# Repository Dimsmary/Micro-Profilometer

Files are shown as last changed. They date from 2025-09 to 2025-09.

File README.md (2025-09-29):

# Micro-Profilometer 微米级轮廓仪

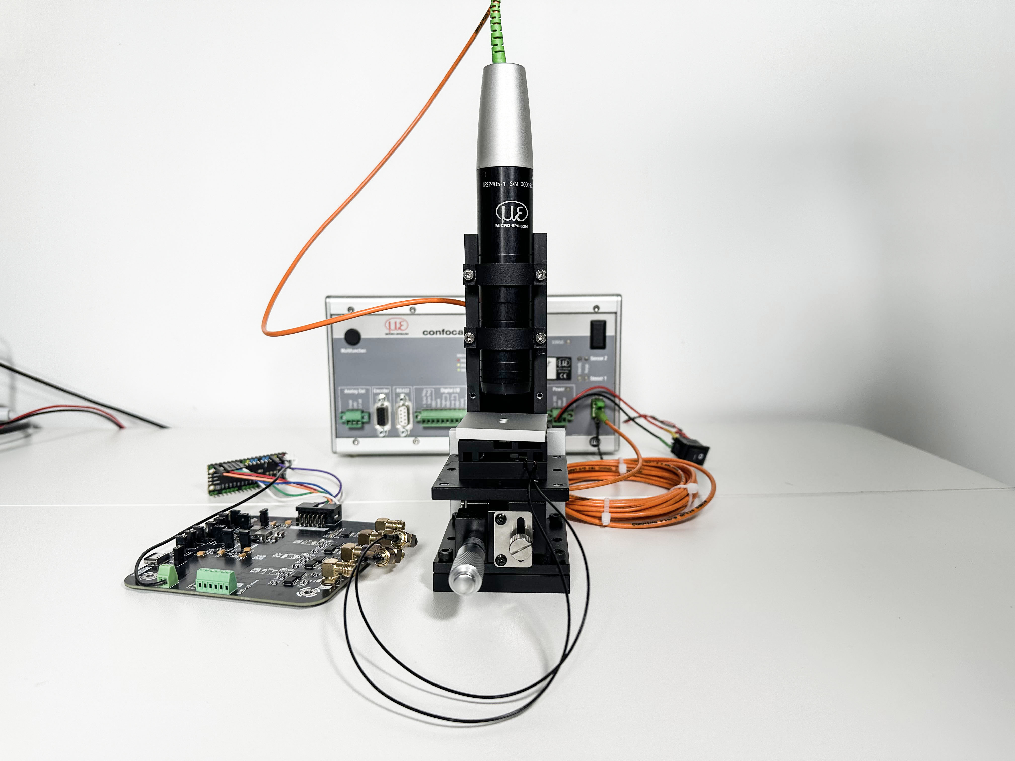
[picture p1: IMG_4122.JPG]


**[中文](README.md) | [English](README_ENG.md)**

## 项目简介

本项目主要设计了一个**亚微米级定位台**，通过与Micro-Epsilon共聚焦位移传感器进行结合后，设计成为微米级表面轮廓仪。

1、该轮廓仪能够完成对微小样品的表面轮廓测量（如晶圆裸片、金属表面等），分析其表面平整度或起伏结构。动态深度分辨率能够达到38nm，横纵分辨率能够达到8μm。

2、对于亚纳米级定位台，其分辨率能够达到100nm。基于该定位台，能够实现包括但不限于：扫描成像（如本项目所示的轮廓仪）、微流控操纵、光学对准等功能。

## 性能表现

### 亚微米级定位台

该定位台为基于粘-滑效应工作原理，具体分析可参考文章：

Open STM: A low-cost scanning tunneling microscope with a fast approach method

https://www.sciencedirect.com/science/article/pii/S2468067223001116

Low-cost, open-source XYZ nanopositioner for high-precision analytical applications

https://www.sciencedirect.com/science/article/pii/S2468067222000621

位移测试通过IFC2421共聚焦位移传感器与IFS2405-1探头完成，采样率为1ksps。

#### 最小步长（5V锯齿波）

在对压电陶瓷施加5Vp-p的锯齿波时，定位台所产生的位移为100nm左右。

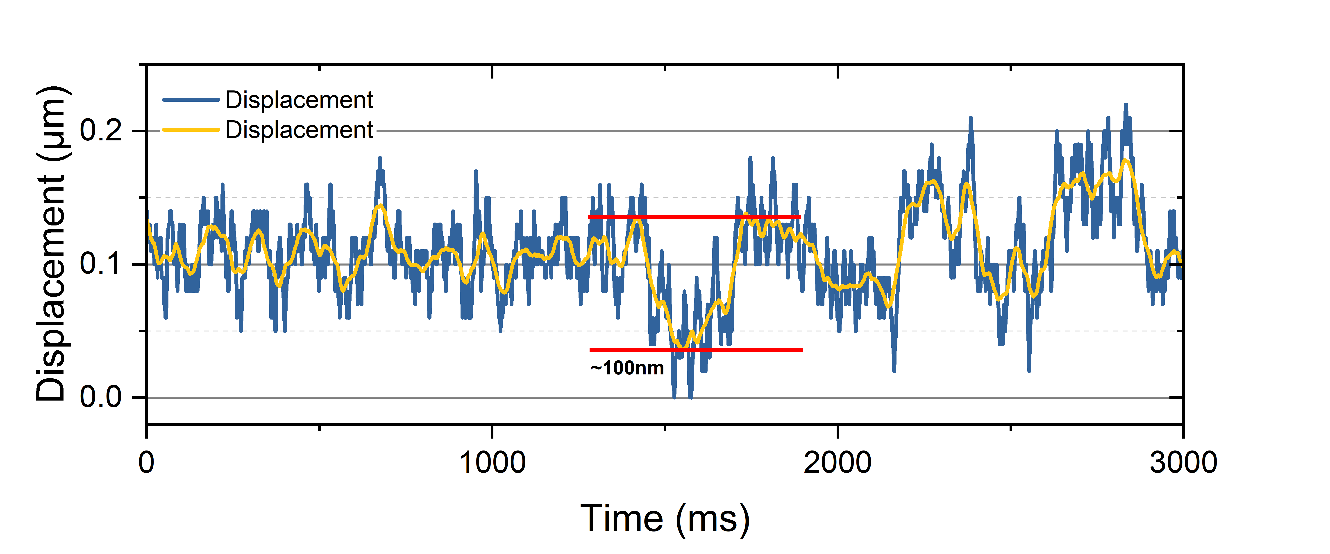
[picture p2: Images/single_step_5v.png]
Single Step 5V


#### 稳定步长（10V锯齿波）

在实际测试过程中，过低的锯齿波电压可能导致位移的不稳定。随着驱动电压的增加，定位台的位移将趋于稳定，以下是10V锯齿波驱动下的单步位移情况。（对于无需反向移动的情况，基于AL1.65型压电陶瓷的单步电压可增加至20Vp-p）

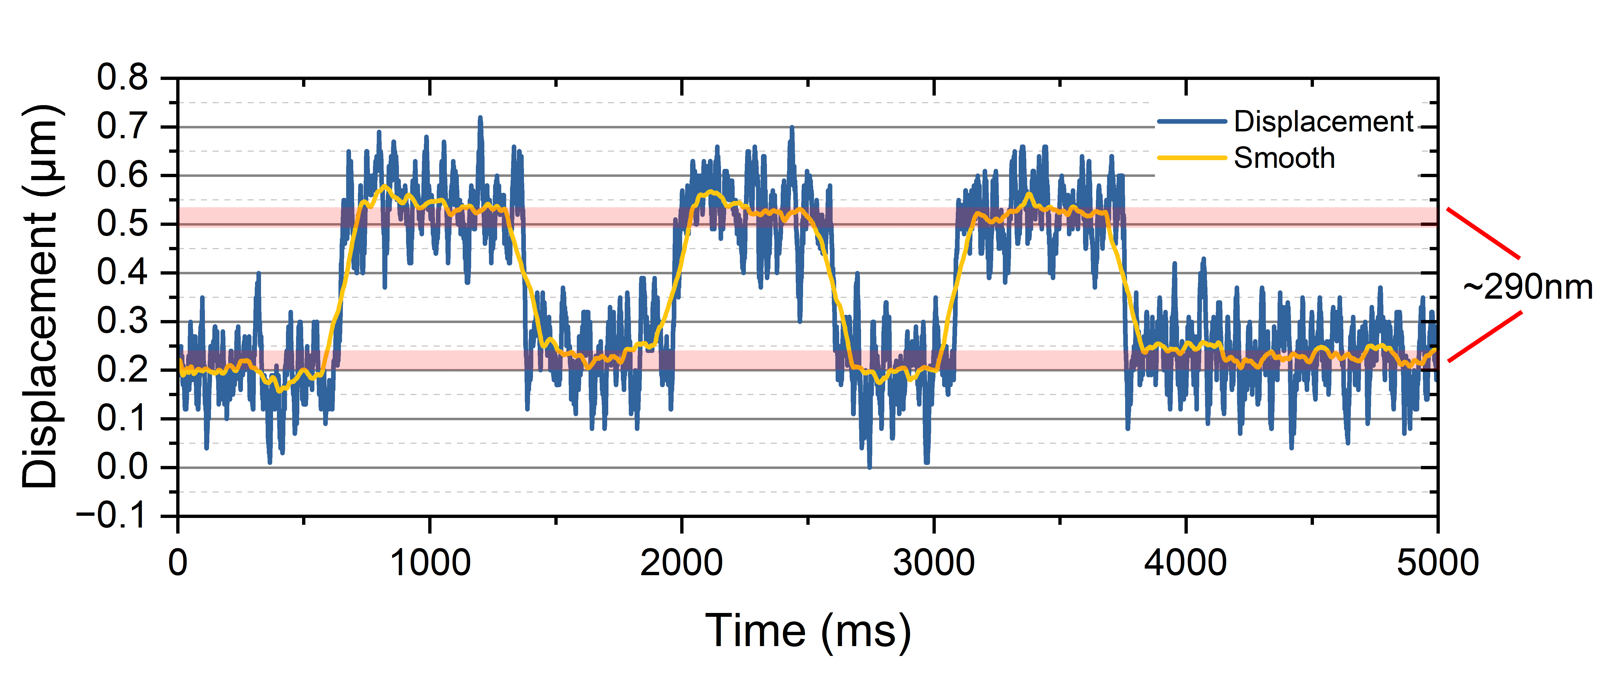
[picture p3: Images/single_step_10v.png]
Single Step 10V


#### 稳定步长（10V锯齿波x10）

通过施加10个连续的10V锯齿波，可以实现2μm左右的单向稳定位移。

在下图所示的过程中，反向位移略小于正向位移，这可能是磁铁与滑轨产生了倾斜导致的。在部分的测试结果中，正向与方向位移能够接近。

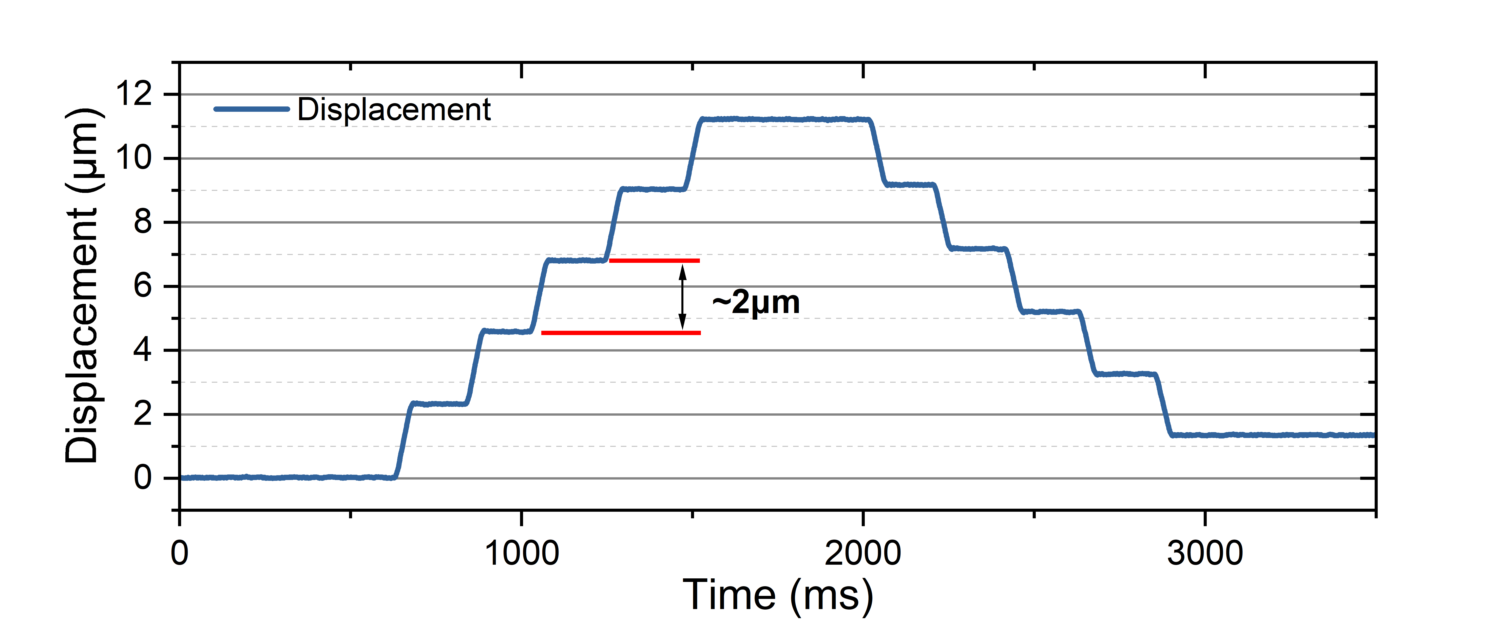
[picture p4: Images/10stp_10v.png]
10Steps 10V


#### 最高速度测试

通过改变锯齿波斜率，测试定位台能够达到的最高速度。如下图所示，定位台的最高速度能够大大0.85mm/s。

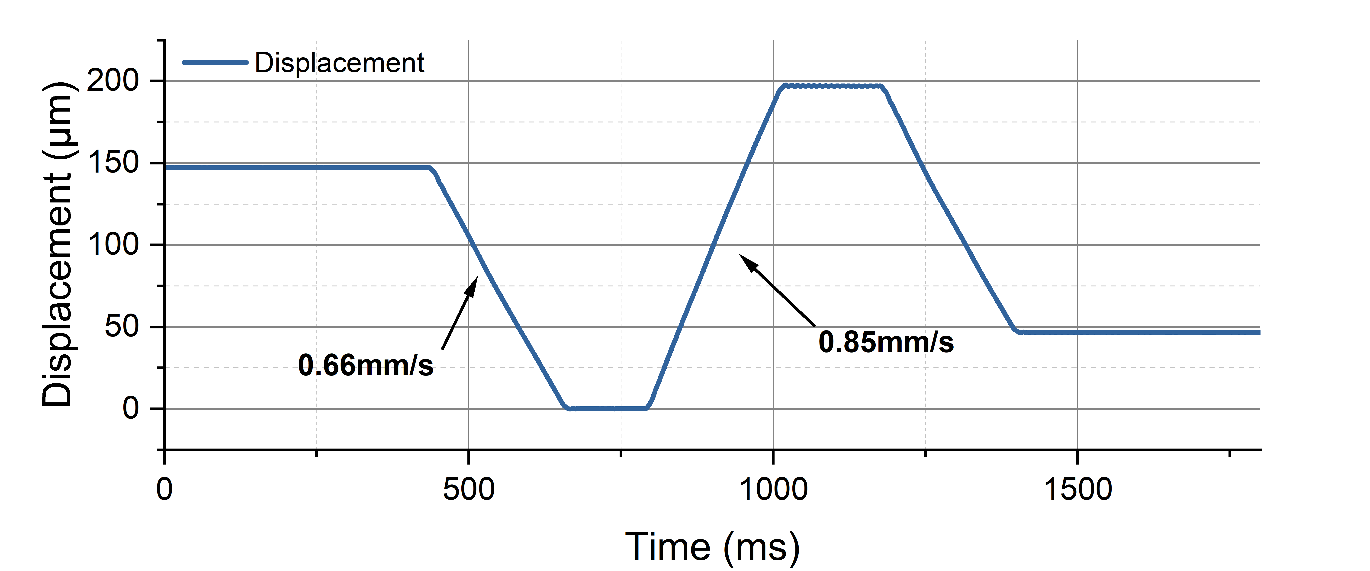
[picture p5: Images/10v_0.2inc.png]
Speed Test


### 微米级轮廓仪

通过将定位台与共聚焦位移传感器结合，设计成为微米级轮廓仪。在工作过程中，定位台进行蛇形扫描，共聚焦传感器采集位移数据，经上位机整合后采集成图像。注意，以下图片的单位**均为微米**。

原始数据可以在ScanImages>RawImage中被找到。其中，xxxs.tiff为灰度映射至[0~255]的版本，以方便直接查看。原始图像需要使用Gwyddion或其他相关软件进行查看。

#### 晶圆裸片

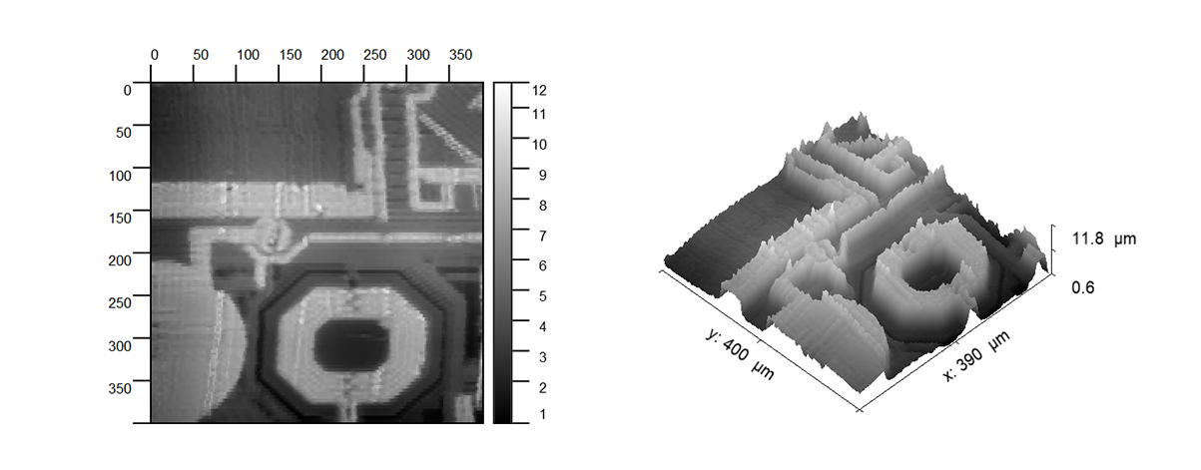
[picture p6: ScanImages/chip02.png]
chip02


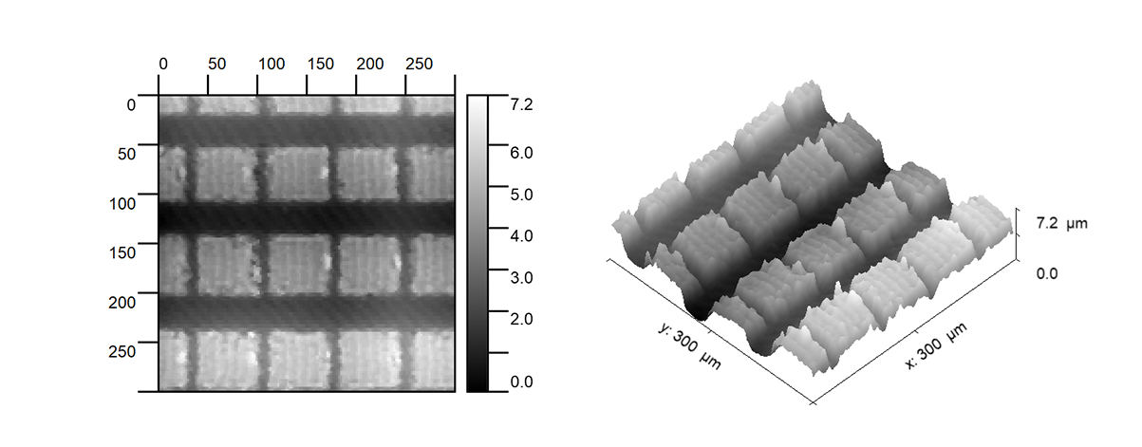
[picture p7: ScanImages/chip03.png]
chip03


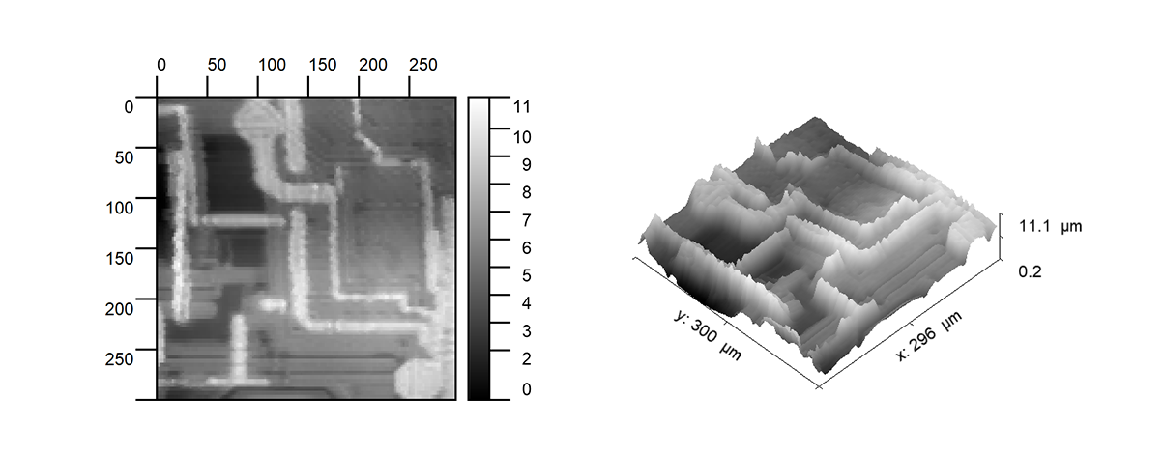
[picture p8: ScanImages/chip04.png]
chip04


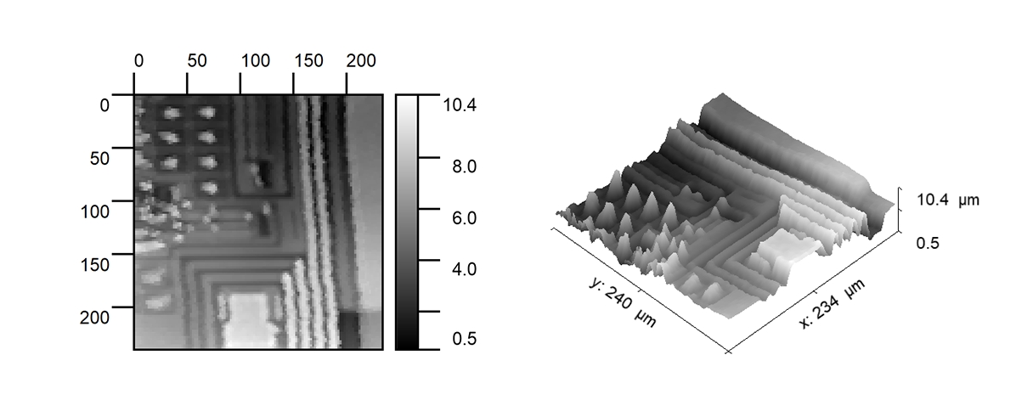
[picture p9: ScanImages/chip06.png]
chip06


#### 阳极氧化铝表面

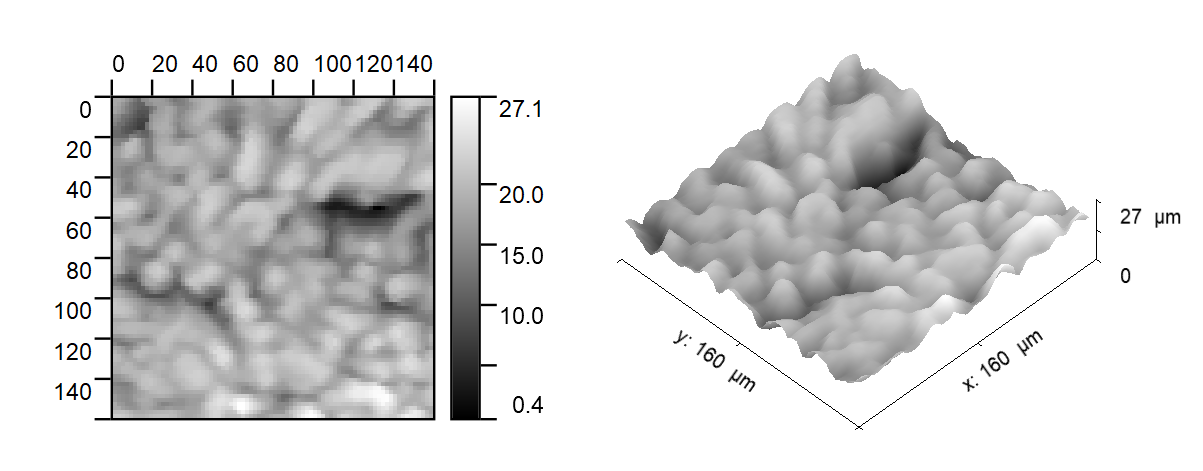
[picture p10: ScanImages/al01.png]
al01


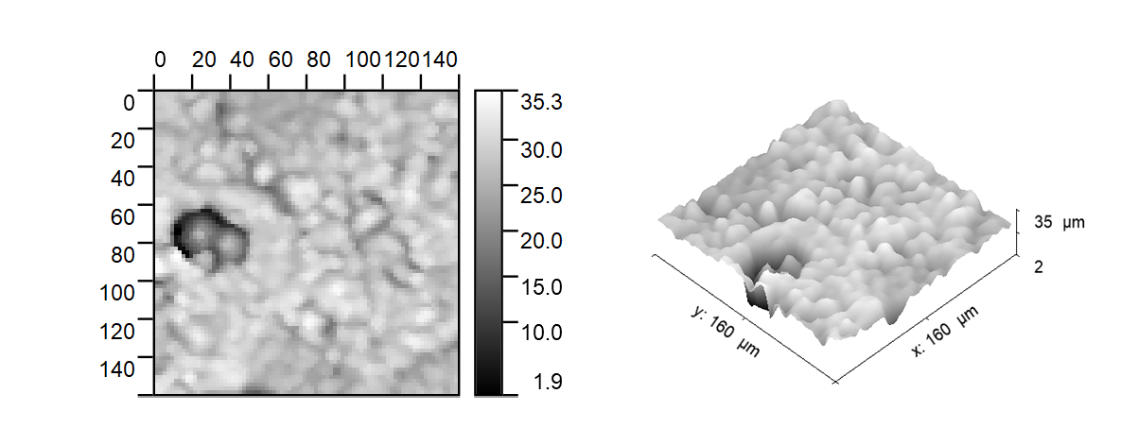
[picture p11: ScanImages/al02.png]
al02


#### 苹果表面

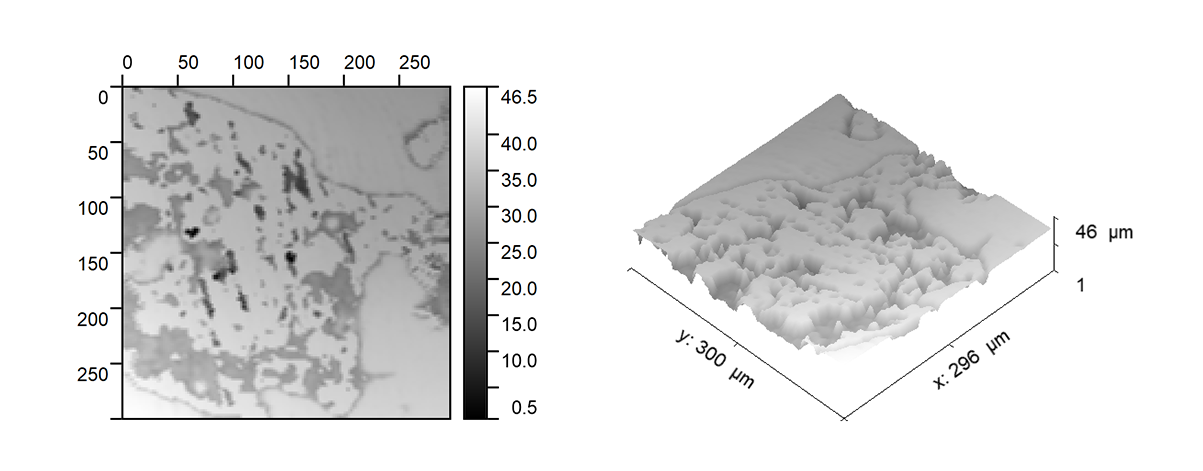
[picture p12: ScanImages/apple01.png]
apple01


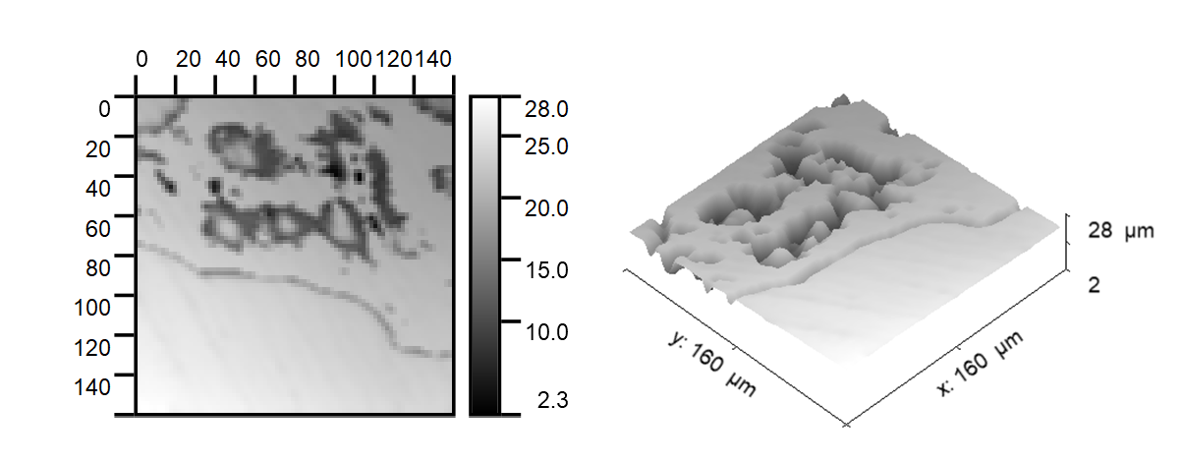
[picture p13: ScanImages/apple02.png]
apple02


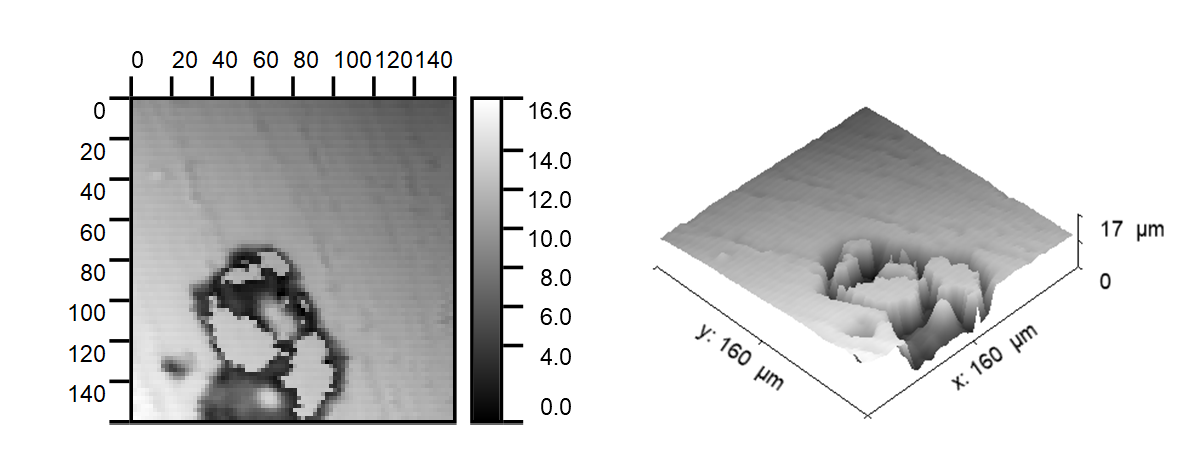
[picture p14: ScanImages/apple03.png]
apple03


#### 纸张表面

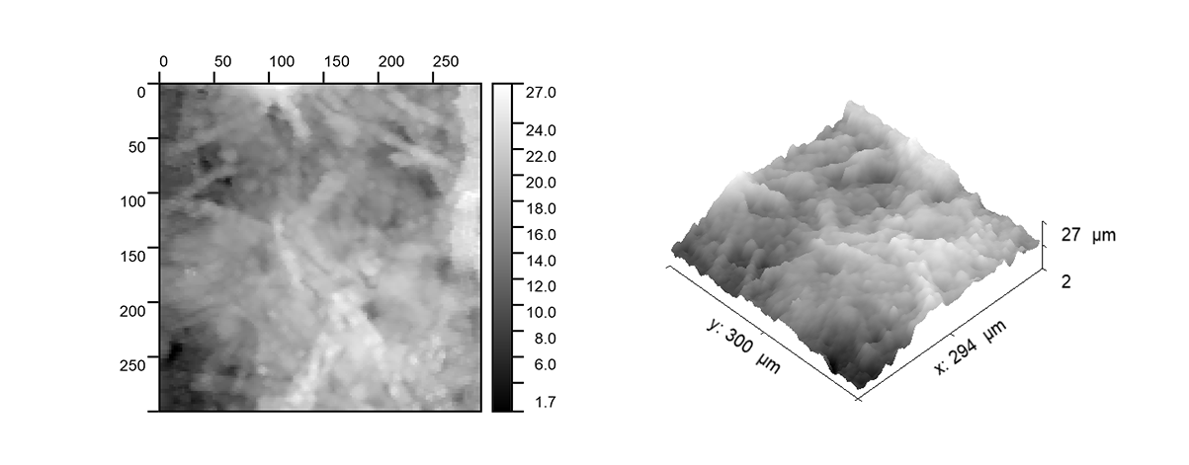
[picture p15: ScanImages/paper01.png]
paper01


#### 纸巾表面

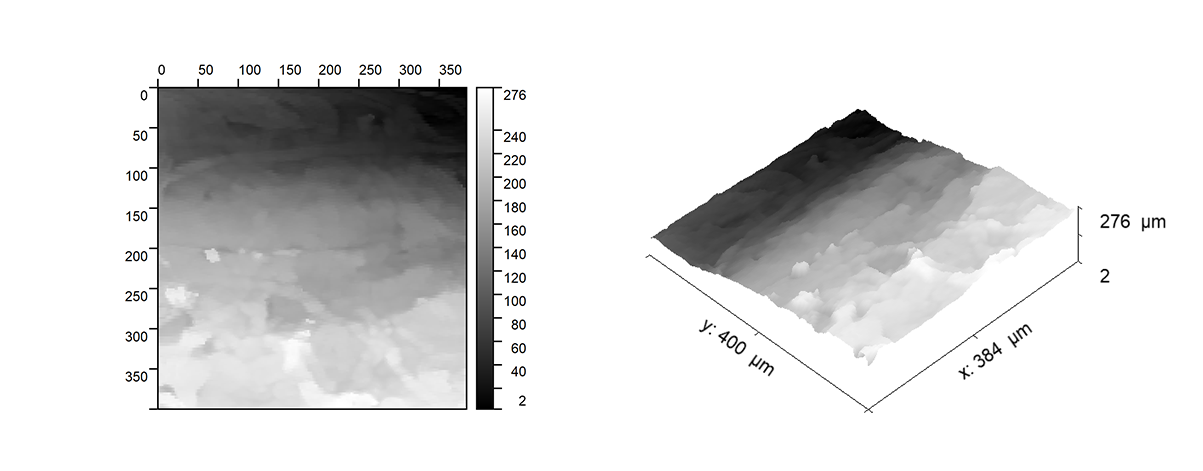
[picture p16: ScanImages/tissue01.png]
tissue01


## 文件目录介绍

3DModel > 包含了项目所有的3D文件

3DModel > CNC > 包含了项目需要加工的CNC文件

3DModel > SolidWorks > 包含了项目的3D原始工程文件

ControlSoftware > 包含了项目使用到的脚本，请安装requirements.txt对应的pip包后运行gui.py以启动上位机

ControlSoftware > reverse.py 用于高度反转

Images > 包含压电滑台的性能数据

Pico2Firmware > 树莓派Pico2固件

ScanImages > 轮廓仪的扫描原始结果

PCB > 工程的PCB文件，请使用EasyEDA/立创EDA打开。或在线打开：https://oshwhub.com/dimsmary/micron-profilometer-micro-profil

## 复刻步骤

### PCB复刻

按照PCB文件夹下提供的文件进行复刻即可。有以下注意事项：

- 对于+5V LDO、DAC3、ADC区域电路为非必要部分，如无需求，可不进行焊接。
- 对于DAC部分的电路，如果DAC采用AD5761R，则ADR421可不进行焊接。如果采用AD5761，则需要进行焊接。对于本项目，默认采用AD5761R。AD5761R与AD5761在寄存器操作时略有不同，后续将进行介绍。

### 固件烧录

请使用VS Code打开Pico2Firmware>Table_Movement进行烧录，或使用Pico2Firmware目录下的.uf2文件完成烧录。

如果需要修改AD5761/AD5761R的初始化设置，请修改Table_Movement>lib>ad57x1>ad57x1.cpp中的\#define CONTROL_REG_BASE，该宏定义对AD5761/AD5761R的初始化进行了设置，包括内部参考电压源的开启/关闭，详情请参考对于数据手册的CONTROL REGISTER小节。

### 零件组装

所有需要加工的文件被放置在了3DModel > CNC下，请参考视频[链接待更新]或3DModel > SolidWorks下的XYTable.SLDASM以及full_assemble.SLDASM进行组装。

- 对于需要额外购买的Z轴定位台，其关键词为[Z轴升降台]，台面尺寸为60x60cm，行程为1cm。

- 对于fix.STEP，可以采用3D打印。
- 定位台的组装可参考[OpenSTM项目](https://github.com/Dimsmary/OpenSTM)，或对应的HardwareX文章：https://doi.org/10.1016/j.ohx.2023.e00504。需要注意的是，在组装定位台时，需要将磁铁侧壁打磨光滑，否则定位台的行程可能受到影响。
- PCB中的Connector通过M2螺丝安装在XYTable_X中，G连接压电陶瓷的负极，X/Y连接压电陶瓷的正极。对于Y轴压电陶瓷的走线已预留槽位，可使用漆包线连接至此PCB。

## 使用方法

### 控制板设置与连接

#### 电源跳线设置

对于PCB电源跳线帽部分的连接，其顺序为（对于三脚，不连则为选择中间，连接中间与另外一端则为选择另外一端）：

SYNC/FREQ: 2.4M

SEQ: SEQ.

SLEW: NORM.

EN1:ON

EN2:OFF

SS: 连接

V_EN: 连接

COMP1: GND

COMP2: GND

#### 数据线连接

SYN1、SYN2连接至GPIO17、20，SDI2、SCK2连接至SPI0的数据输出、时钟引脚。

#### 电源连接

使用5V Type-C口电源连接至Power_IN端。

#### 与定位台的连接

使用SMA-IPEX连接线，将DAC0、DAC1与定位台中的Connector PCB连接。

### PC-USB连接

将PICO2连接至PC，此时PICO2将在PC处初始化两个虚拟串口。

使用RS422转USB连接Micro-Epsilon共聚焦位移传感器与PC，在Micro-Epsilon的设置中，需要设置仅输出Distance1。

### 上位机使用

运行gui.py启动上位机。

上位机包含四个选项卡：Serial Ports, DAC Manual Control, Sawtooth Control, Scan。

#### Serial Ports

在Serial Ports中，moving table port连接PICO2的虚拟串口，连接数字较大的一个。（如，PICO2提供了COM12和COM13，连接COM13）。confocal port连接RS422转USB。

#### DAC Manual Control

在DAC Manual Control中，可以对DAC0/1的输出电压控制。如果需要控制DAC3，可以将SYN3连接至GPIO21。

#### Sawtooth Control

在Sawtooth Control中，可以控制DAC0/1发送锯齿波。以下是参数解释：

Sawtooth Steps：锯齿波数量。

Increment：电压每步增量，单位：V。

Maximum Voltage：锯齿波电压峰值。

Bias Voltage：锯齿波初始电压。

Channel Select：输出端口选择，X channel则为DAC0，Y Channel则为DAC1。

在参数修改后，需要点击Sync Settings进行参数同步。

点击Send Positive Sawtooth则会发送正锯齿波，Send Negative Sawtooth则会发送负锯齿波。

#### Scan

在Scan中，可以对样品轮廓进行扫描。

X Forward Steps：扫描过程中，X定位台的单步前进的锯齿波数。

X Backward Steps：扫描过程中，X定位台的单步后退锯齿波数。

Y Forward Steps：扫描过程中，Y定位台的单步前进锯齿波数。

Y Backward Steps：暂时不使用

Image Size X：图像X尺寸

Image Size Y：图像Y尺寸

Increment：暂时不使用

点击Start Monitor后，共聚焦传感器的位移值将实时显示在图像框的上方。将各参数值设置好后，点击Scan开始扫描。

需要注意的是，考虑到定位台的正向位移和反向位移可能不一致，可以设置不同的X Forward/Backward Steps值。当你观察到图像不对劲时，可以尝试保持Forward值，然后增加或减少Backward值直到图像正常。

在完成扫描后，图像将被显示在图像框中，点击Save Image即可对图像进行保存。图像将被保存为两张，其中带_scaled后缀的图像的灰度值将被映射至0~255以便浏览。

## 最后

如果你有任何问题，欢迎提交Issue。

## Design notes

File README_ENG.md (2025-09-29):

# Micro-Profilometer



**[中文](README.md) | [English](README_ENG.md)**

## Project Overview

This project primarily designs a **sub-micron positioning stage**. By integrating it with a Micro-Epsilon confocal displacement sensor, it is developed into a micron-level surface profilometer.

1. This profilometer can measure the surface profile of small samples (such as wafer dies, metal surfaces, etc.), analyzing their surface flatness or topographic features. It achieves a dynamic depth resolution of 38nm and lateral resolutions of 8μm.
2. For the sub-micron positioning stage, its resolution reaches 100nm. Based on this stage, various functions can be implemented, including but not limited to: scanning imaging (as demonstrated by this profilometer project), microfluidic manipulation, optical alignment, etc.

## Performance

### Sub-Micron Positioning Stage

This positioning stage operates based on the stick-slip principle. For detailed analysis, please refer to the articles:

Open STM: A low-cost scanning tunneling microscope with a fast approach method

https://www.sciencedirect.com/science/article/pii/S2468067223001116

Low-cost, open-source XYZ nanopositioner for high-precision analytical applications

https://www.sciencedirect.com/science/article/pii/S2468067222000621

Displacement testing was completed using an IFC2421 confocal displacement sensor with an IFS2405-1 probe, at a sampling rate of 1 ksps.

#### Minimum Step (5V Sawtooth Wave)

When a 5Vp-p sawtooth wave is applied to the piezoelectric ceramic, the displacement generated by the positioning stage is about 100nm.

Single Step 5V

#### Stable Step (10V Sawtooth Wave)

During practical testing, excessively low sawtooth wave voltage may lead to unstable displacement. As the driving voltage increases, the stage's displacement becomes more stable. The following shows the single-step displacement under a 10V sawtooth wave drive. (For scenarios not requiring reverse movement, the single-step voltage for the AL1.65 type piezoelectric ceramic can be increased up to 20Vp-p).

Single Step 10V

#### Stable Steps (10V Sawtooth Wave x10)

By applying 10 consecutive 10V sawtooth waves, a unidirectional stable displacement of about 2μm can be achieved.

In the process shown below, the reverse displacement is slightly less than the forward displacement, which might be caused by tilting between the magnet and the slide rail. In some test results, the forward and reverse displacements can be close.

10Steps 10V

#### Maximum Speed Test

By changing the slope of the sawtooth wave, the maximum speed achievable by the positioning stage was tested. As shown below, the maximum speed of the stage can reach 0.85 mm/s.

Speed Test

### Micron-Level Profilometer

By integrating the positioning stage with the confocal displacement sensor, a micron-level profilometer is constructed. During operation, the positioning stage performs a raster scan, the confocal sensor collects displacement data, and the host computer integrates this data to form an image. Note that the units in the following images are **all in micrometers**.

Raw data can be found in `ScanImages > RawImage`. Among them, files with the `xxxs.tiff` suffix are versions with grayscale mapped to [0~255] for direct viewing. The original images need to be viewed using Gwyddion or other relevant software.

#### Wafer Die

chip02

chip03

chip04

chip06

#### Anodized Aluminum Surface

al01

al02

#### Apple Surface

apple01

apple02

apple03

#### Paper Surface

paper01

#### Tissue Paper Surface

tissue01

## Directory Structure

`3DModel` > Contains all 3D files for the project

`3DModel > CNC` > Contains CNC files required for project fabrication

`3DModel > SolidWorks` > Contains the original 3D engineering files for the project

`ControlSoftware` > Contains scripts used in the project. Please install the pip packages listed in `requirements.txt` and run `gui.py` to start the host computer software.

`ControlSoftware > reverse.py` > Used for height inversion.

`Images` > Contains performance data for the piezoelectric stage.

`Pico2Firmware` > Raspberry Pi Pico 2 firmware.

`ScanImages` > Raw scanning results from the profilometer.

`PCB` > PCB files for the project. Please open using EasyEDA/JiLiang EDA. Or open online:https://oshwhub.com/dimsmary/micron-profilometer-micro-profil

## Replication Steps

### PCB Replication

- Replicate according to the files provided in the PCB folder. Note the following:
  - The circuits for the +5V LDO, DAC3, and ADC areas are non-essential and can be left unsoldered if not required.
  - For the DAC section circuit: If using the AD5761R DAC, the ADR421 does not need to be soldered. If using the AD5761, it must be soldered. This project defaults to using the AD5761R. Note that register operations for the AD5761R and AD5761 differ slightly; this will be explained later.

### Firmware Flashing

Please use VS Code to open `Pico2Firmware > Table_Movement` for flashing, or use the `.uf2` file in the `Pico2Firmware` directory to flash.

If you need to modify the AD5761/AD5761R initialization settings, please modify the `#define CONTROL_REG_BASE` in `Table_Movement > lib > ad57x1 > ad57x1.cpp`. This macro definition sets the initialization for the AD5761/AD5761R, including enabling/disabling the internal reference voltage source. Please refer to the CONTROL REGISTER section of the respective datasheet for details.

### Parts Assembly

- All files requiring machining are located in `3DModel > CNC`. Please refer to the video [Link to be updated] or the `XYTable.SLDASM` and `full_assemble.SLDASM` files under `3DModel > SolidWorks` for assembly.
  - For the additionally purchasable Z-axis stage, search using the keyword `[Z-axis lifting stage]`, with a platform size of 60x60mm and a travel of 1cm.
  - For `fix.STEP`, 3D printing can be used.
  - The assembly of the positioning stage can refer to the [OpenSTM project](https://github.com/Dimsmary/OpenSTM), or the corresponding HardwareX article: https://doi.org/10.1016/j.ohx.2023.e00504. Note that when assembling the positioning stage, the sidewalls of the magnets need to be polished smooth, otherwise the travel range of the stage might be affected.
  - The Connector on the PCB is mounted on the `XYTable_X` using M2 screws. `G` connects to the negative terminal of the piezoelectric ceramic, `X`/`Y` connect to the positive terminals of the piezoelectric ceramics. A slot is reserved for the wiring of the Y-axis piezoelectric ceramic; use enameled wire to connect it to this PCB.

## Usage Instructions

### Control Board Setup and Connection

#### Power Jumper Settings

For the PCB power jumper cap connections, the order is as follows (for three-pin headers, not connecting means selecting the middle pin; connecting the middle and another pin selects that other pin):

- SYNC/FREQ: 2.4M
- SEQ: SEQ.
- SLEW: NORM.
- EN1: ON
- EN2: OFF
- SS: Connect
- V_EN: Connect
- COMP1: GND
- COMP2: GND

#### Data Cable Connection

Connect SYN1, SYN2 to GPIO17, GPIO20. Connect SDI2, SCK2 to the data output and clock pins of SPI0.

#### Power Connection

Use a 5V Type-C power supply connected to the `Power_IN` terminal.

#### Connection to the Positioning Stage

Use SMA-to-IPEX cables to connect DAC0, DAC1 to the Connector PCB on the positioning stage.

#### PC-USB Connection

Connect the PICO2 to the PC. The PICO2 will initialize two virtual COM ports on the PC.

Connect the Micro-Epsilon confocal displacement sensor to the PC using an RS422-to-USB converter. In the Micro-Epsilon settings, configure it to output only `Distance1`.

### Host Computer Software Usage

Run `gui.py` to start the host computer software.

The software interface contains four tabs: `Serial Ports`, `DAC Manual Control`, `Sawtooth Control`, `Scan`.

#### Serial Ports

In the `Serial Ports` tab, connect `moving table port` to the virtual COM port of the PICO2 (connect to the higher numbered port, e.g., if PICO2 provides COM12 and COM13, connect to COM13). Connect `confocal port` to the RS422-to-USB converter.

#### DAC Manual Control

In the `DAC Manual Control` tab, you can manually control the output voltage of DAC0/1. If you need to control DAC3, connect SYN3 to GPIO21.

#### Sawtooth Control

In the `Sawtooth Control` tab, you can control DAC0/1 to send sawtooth waves. Parameter explanations:

- `Sawtooth Steps`: Number of sawtooth waves.
- `Increment`: Voltage increment per step, unit: V.
- `Maximum Voltage`: Peak voltage of the sawtooth wave.
- `Bias Voltage`: Initial voltage of the sawtooth wave.
- `Channel Select`: Output port selection, `X channel` is DAC0, `Y Channel` is DAC1.

After modifying parameters, click `Sync Settings` to synchronize the parameters.

Click `Send Positive Sawtooth` to send a positive sawtooth wave, and `Send Negative Sawtooth` to send a negative sawtooth wave.

#### Scan

In the `Scan` tab, you can perform a raster scan of the sample surface.

- `X Forward Steps`: Number of sawtooth waves for the single-step forward movement of the X stage during scanning.
- `X Backward Steps`: Number of sawtooth waves for the single-step backward movement of the X stage during scanning.
- `Y Forward Steps`: Number of sawtooth waves for the single-step forward movement of the Y stage during scanning.
- `Y Backward Steps`: Not currently used.
- `Image Size X`: Image size in the X dimension.
- `Image Size Y`: Image size in the Y dimension.
- `Increment`: Not currently used.

Click `Start Monitor` to display the real-time displacement value from the confocal sensor above the image box. After setting all parameter values, click `Scan` to start the scan.

Note: Considering that the forward and reverse displacements of the positioning stage might not be equal, you can set different values for `X Forward Steps` and `X Backward Steps`. If you observe that the image looks distorted, try keeping the `Forward` value and then increasing or decreasing the `Backward` value until the image appears normal.

After the scan is complete, the image will be displayed in the image box. Click `Save Image` to save the image. Two images will be saved; the one with the `_scaled` suffix has its grayscale values mapped to 0~255 for easier viewing.

## Finally

If you have any questions, please feel free to submit an Issue.

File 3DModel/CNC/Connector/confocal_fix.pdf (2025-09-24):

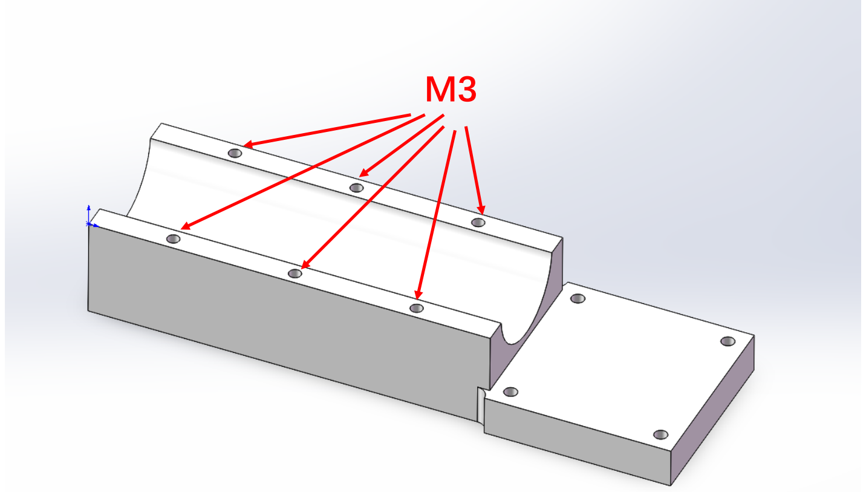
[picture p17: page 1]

M3

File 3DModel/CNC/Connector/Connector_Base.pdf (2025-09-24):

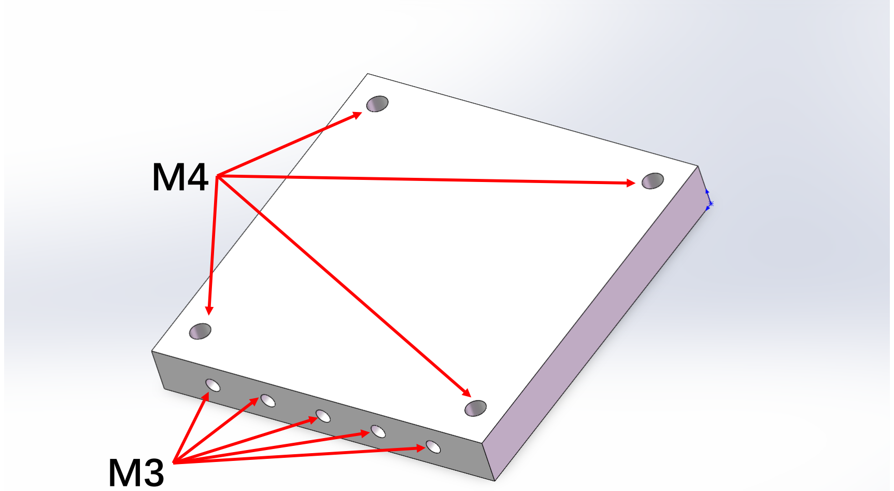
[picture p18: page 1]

M4

M3

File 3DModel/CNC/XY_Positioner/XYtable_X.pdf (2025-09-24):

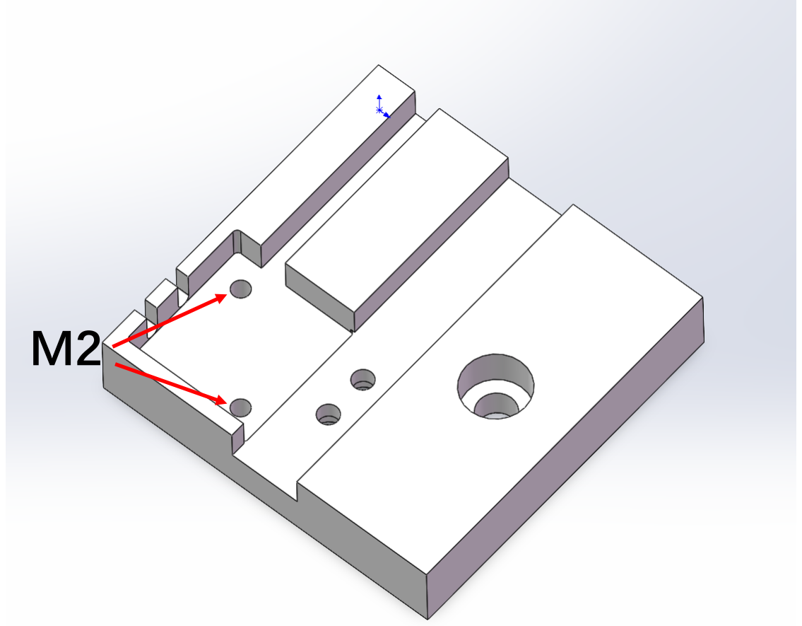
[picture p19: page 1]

M2

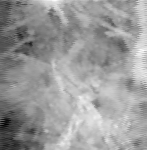
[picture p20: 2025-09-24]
ScanImages/RawImage/paper01.tiff

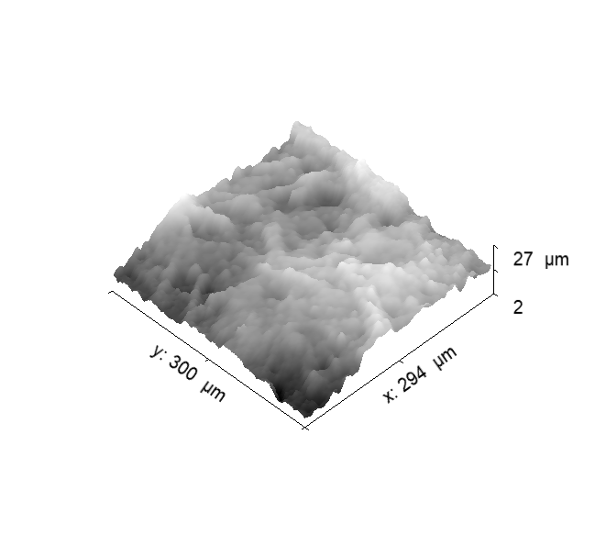
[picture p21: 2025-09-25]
ScanImages/Processed/paper01.png

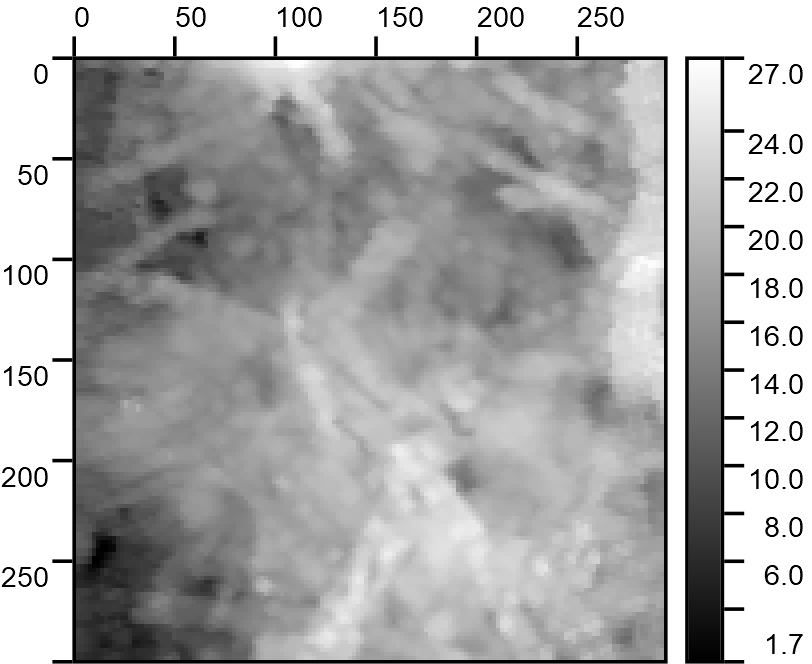
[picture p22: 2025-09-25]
ScanImages/Processed/paper01.tiff

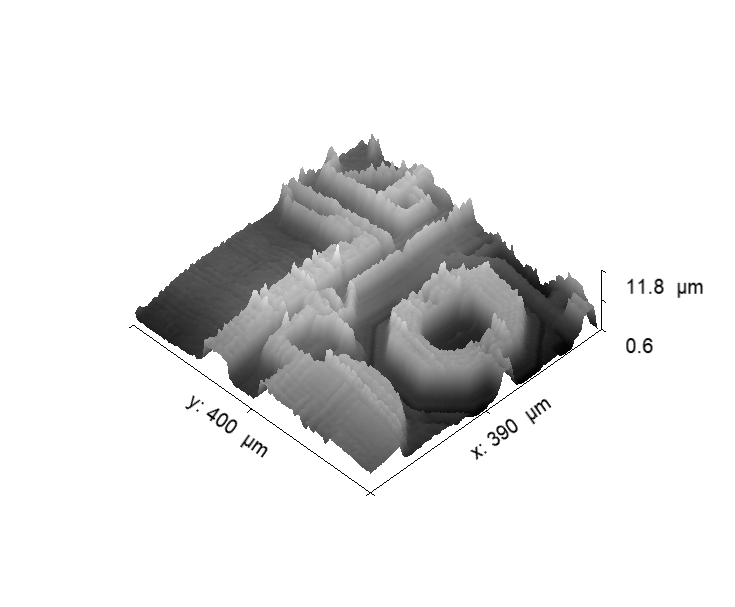
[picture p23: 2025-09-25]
ScanImages/Processed/chip02.png

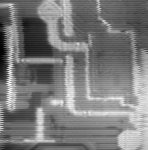
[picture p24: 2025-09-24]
ScanImages/RawImage/chip04s.tiff

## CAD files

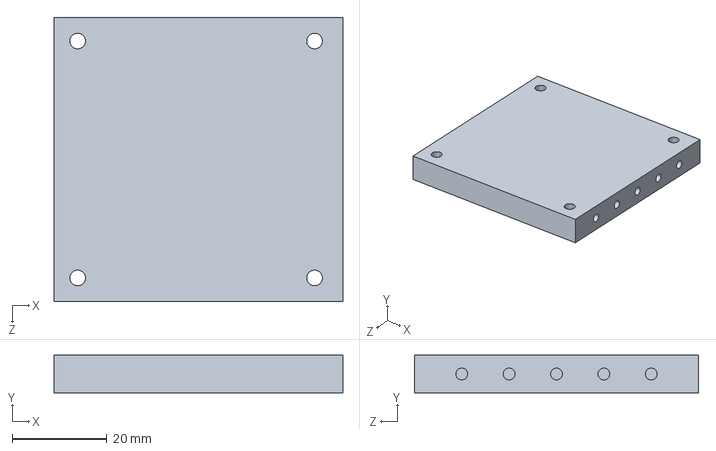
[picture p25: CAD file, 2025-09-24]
3DModel/CNC/Connector/Connector_Base.STEP
61.0 x 8.00 x 60.0 mm

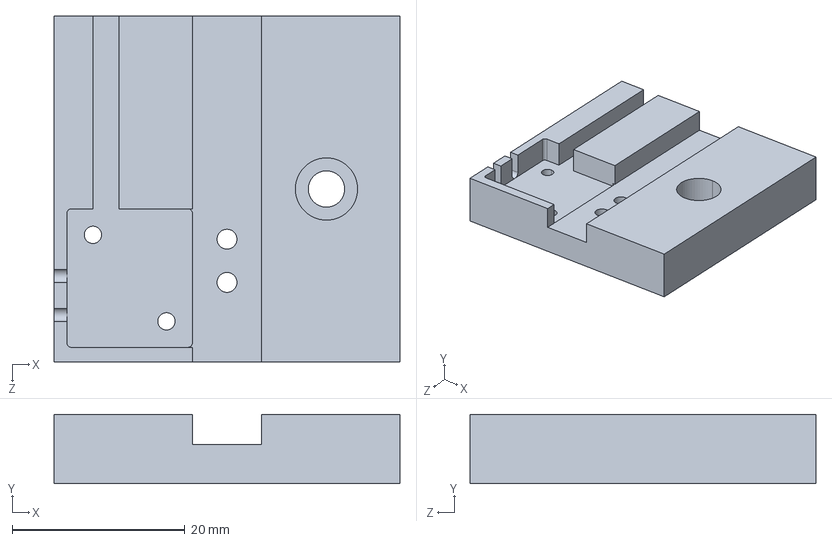
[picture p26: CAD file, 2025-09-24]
3DModel/CNC/XY_Positioner/XYTable_X.STEP
40.0 x 8.00 x 40.0 mm

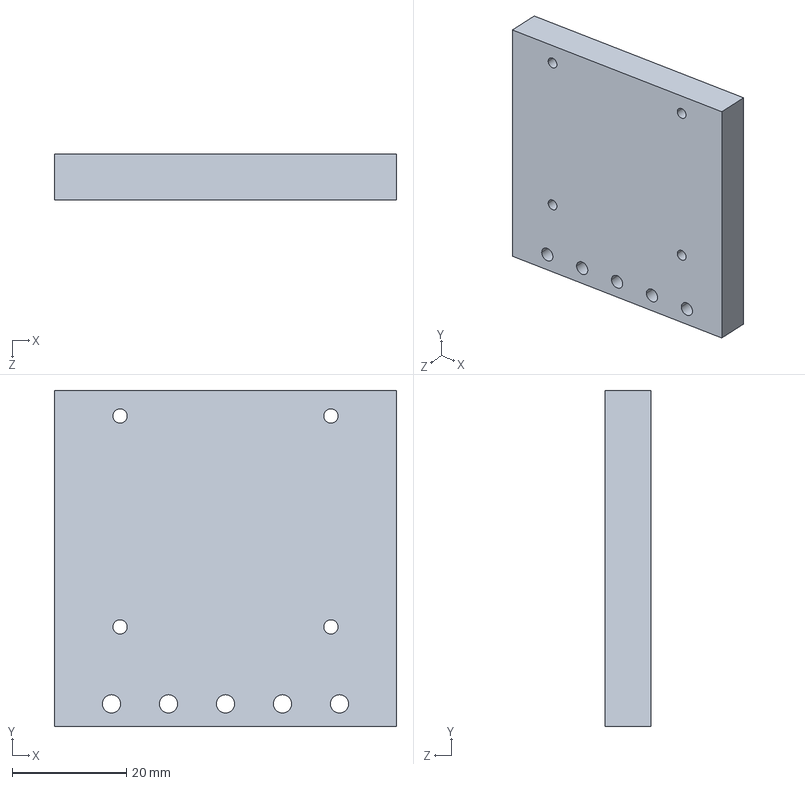
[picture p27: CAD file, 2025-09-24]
3DModel/CNC/Connector/Connector_Side.STEP
60.0 x 59.0 x 8.00 mm

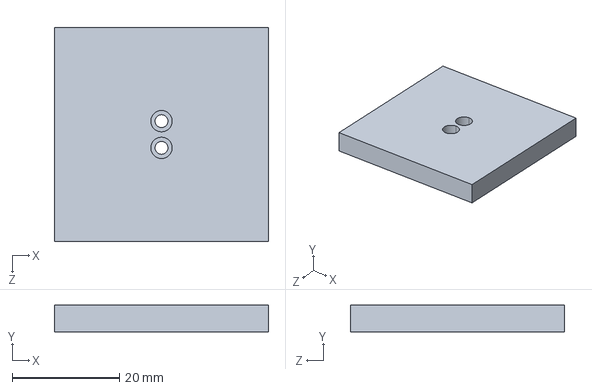
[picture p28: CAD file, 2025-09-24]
3DModel/CNC/XY_Positioner/XYTable_Table.STEP
40.0 x 5.00 x 40.0 mm

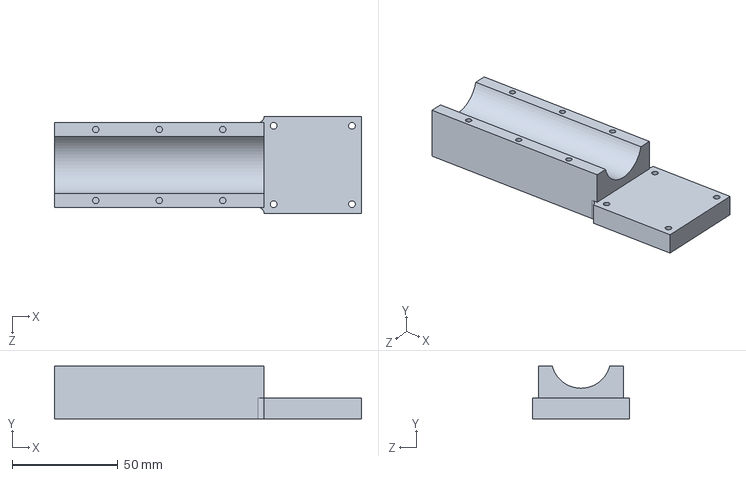
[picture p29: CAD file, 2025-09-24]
3DModel/CNC/Connector/confocal_fix.STEP
145.0 x 25.0 x 46.0 mm

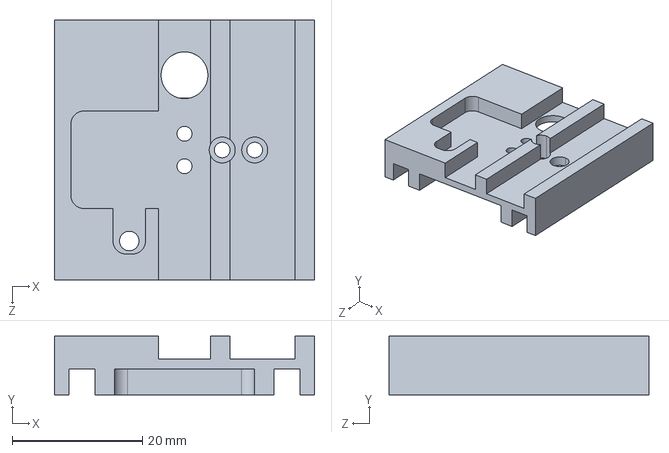
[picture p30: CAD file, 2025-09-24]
3DModel/CNC/XY_Positioner/XYTable_Y.STEP
40.0 x 9.00 x 40.0 mm

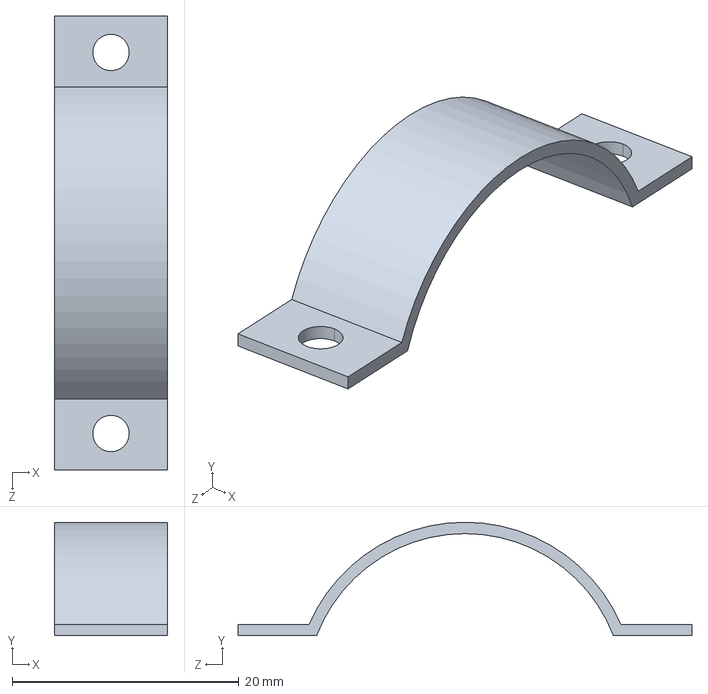
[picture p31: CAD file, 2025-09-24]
3DModel/CNC/Connector/fix.STEP
10.0 x 10.0 x 40.0 mm

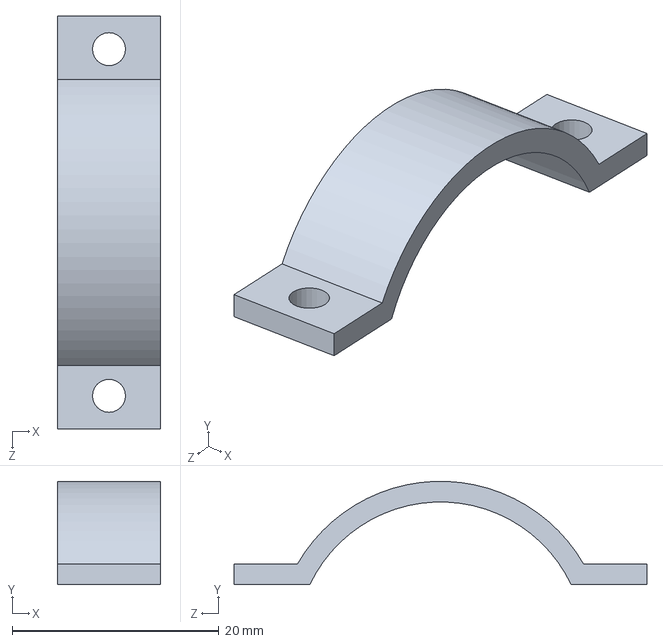
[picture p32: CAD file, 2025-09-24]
3DModel/Solidworks/fix.SLDPRT
10.0 x 9.99 x 40.0 mm

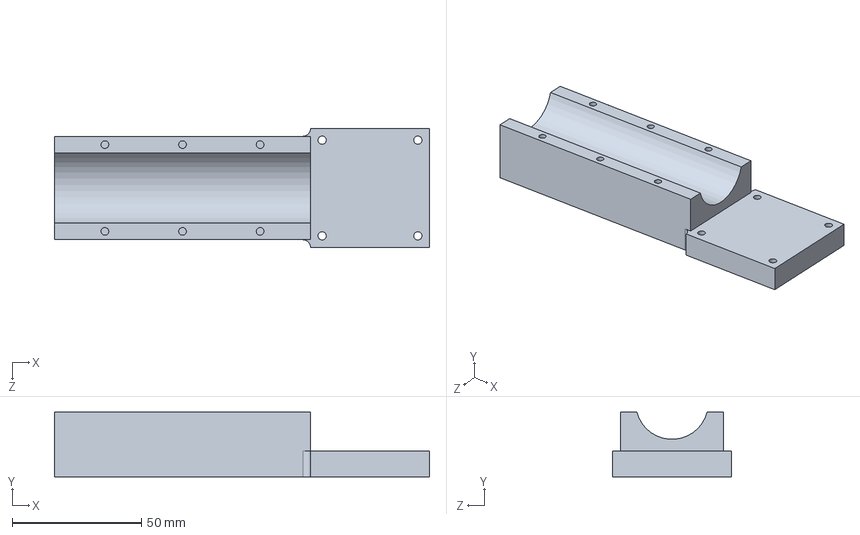
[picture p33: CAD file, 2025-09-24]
3DModel/Solidworks/confocal_fix.SLDPRT
145.0 x 25.0 x 46.0 mm

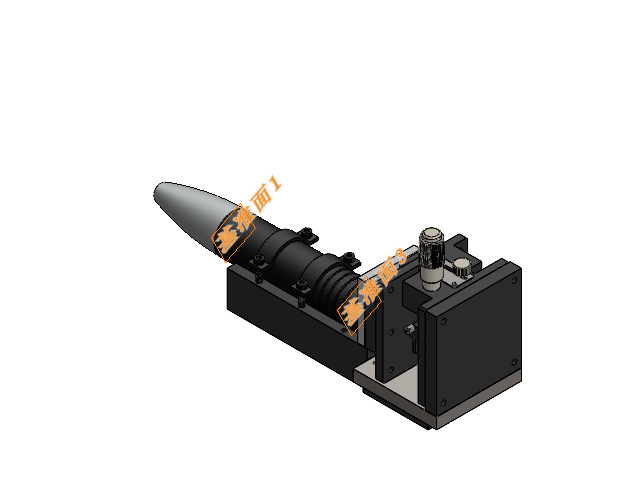
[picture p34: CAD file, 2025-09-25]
3DModel/SolidWorks/full_assemble.SLDASM
confocal_fix
Connector_Side
screw_M3-10 x 4
confocal
fix x 2
screw_M3-15 x 4
Connector_Base
ztable
XYTable_X
XYTable_Y
Slider_Bottom x 2
Slider_up x 2
XYTable_Table
screw_M2-4 x 4
pzt x 2
round_megnent x 2

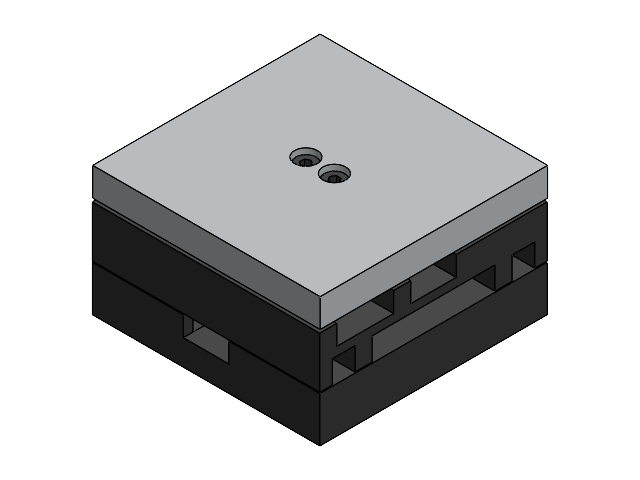
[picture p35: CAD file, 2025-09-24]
3DModel/Solidworks/XYTable.SLDASM
XYTable_X
XYTable_Y
Slider_Bottom x 2
Slider_up x 2
XYTable_Table
screw_M2-4 x 4
pzt x 2
round_megnent x 2

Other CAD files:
3DModel/Solidworks/XYTable_X.SLDPRT
3DModel/Solidworks/XYTable_Y.SLDPRT
3DModel/Solidworks/Connector_Side.SLDPRT
3DModel/Solidworks/XYTable_Table.SLDPRT
3DModel/Solidworks/Connector_Base.SLDPRT

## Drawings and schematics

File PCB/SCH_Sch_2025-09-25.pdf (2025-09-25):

# +12V LDO

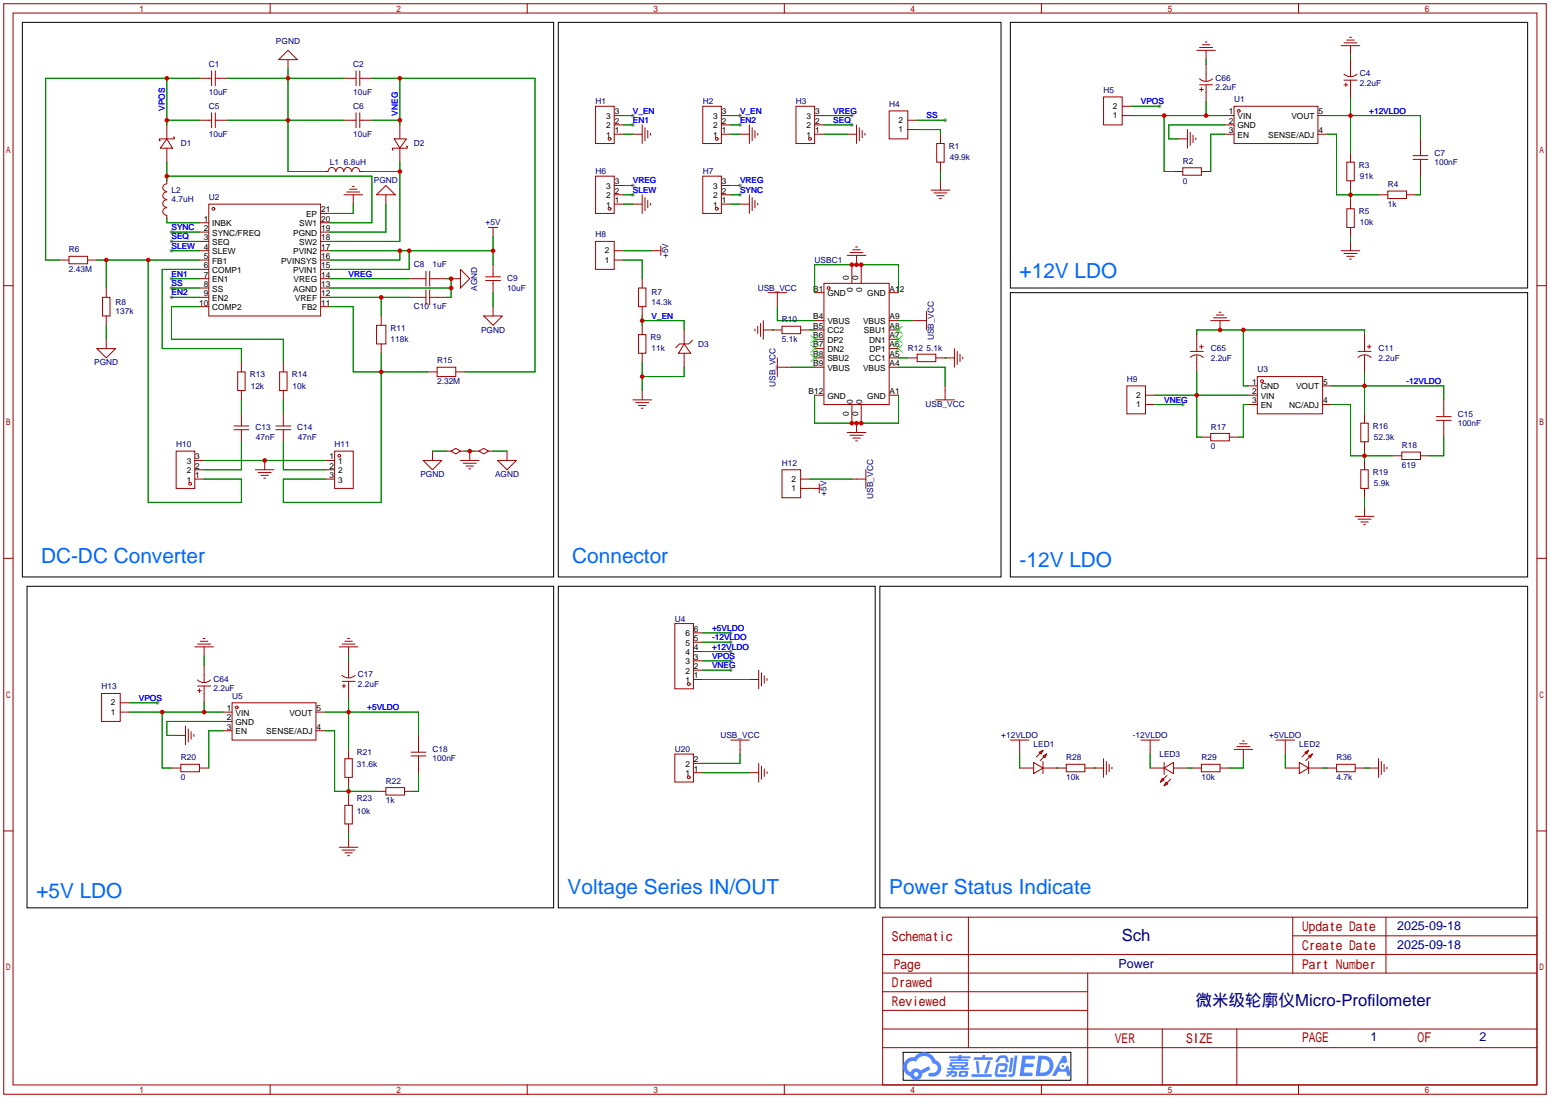
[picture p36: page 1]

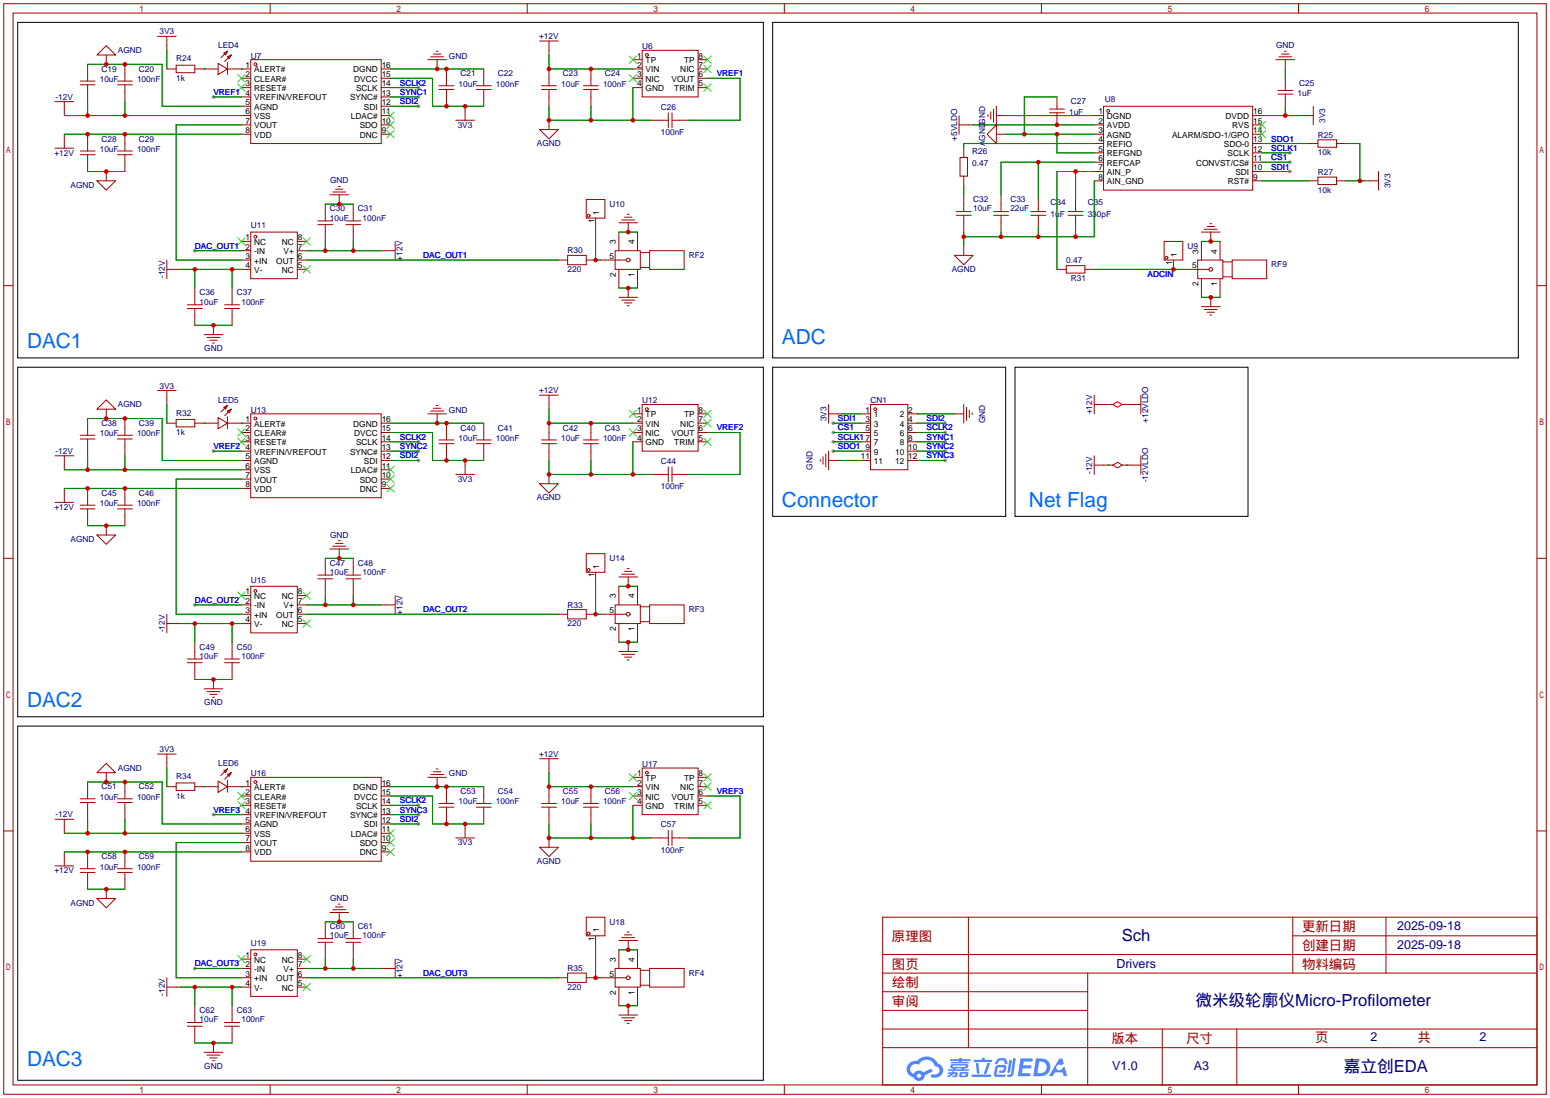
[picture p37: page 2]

SDO 10 LDAC# 11 SDI 12 SYNC# 13 SCLK 14 DVCC 15 DGND 16

SDI 10 CONVST/CS# 11 SCLK 12 SDO-0 13 ALARM/SDO-1/GPO 14 RVS 15 DVDD 16

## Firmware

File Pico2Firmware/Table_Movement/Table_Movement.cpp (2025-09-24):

#include "pico/stdlib.h"
#include "hardware/spi.h"
#include <lib/ad57x1/ad57x1.hpp>
#include <lib/command_handle/command_handle.hpp>

#include <bsp/board_api.h>

uint16_t tri_steps = 1;
float tri_bias_voltage = 0.0f;
float tri_increasement = 0.05f;
float tri_amplitude = 10.0f;
bool tri_x = true;
bool tri_forward = true;

float dac_val = 0.0f;
uint8_t dac_range = 0;
uint8_t dac_num = 0;


bool command_dac = false;
bool command_dac_range = false;
bool command_tri = false;

AD57x1 dac1(spi0, 17); // GPIO17 -> CS1
AD57x1 dac2(spi0, 20); // GPIO20 -> CS2
AD57x1 dac3(spi0, 21); // GPIO21 -> CS3

void generate_sawtooth_wave();

int main() {
    // init CDC UART
    board_init();
    tusb_init();

    stdio_init_all();
    
    // init SPI
    spi_init(spi0, 10 * 1000 * 1000);

    // Set SPI mode2
    spi_set_format(spi0,
                   8, 
                   SPI_CPOL_1, 
                   SPI_CPHA_0, 
                   SPI_MSB_FIRST); 
    gpio_set_function(18, GPIO_FUNC_SPI); // SCK
    gpio_set_function(19, GPIO_FUNC_SPI); // MOSI
    gpio_set_function(16, GPIO_FUNC_SPI); // MISO

    dac1.software_reset();
    dac2.software_reset();
    dac3.software_reset();

    dac1.set_range(0b000);
    dac2.set_range(0b000);
    dac3.set_range(0b000);

    while (true) {
        // TinyUSB device task | must be called regurlarly
        tud_task();
        
        // If there are command wating
        if(command_dac){
            // select dac
            switch (dac_num){
                case 0:
                dac1.write_voltage(dac_val);
                break;

                case 1:
                dac2.write_voltage(dac_val);
                break;

                case 2:
                dac3.write_voltage(dac_val);
                break;
            }
            command_dac = false;
        }

        else if(command_dac_range){
            switch (dac_num){
                case 0:
                dac1.set_range(dac_val);
                break;

                case 1:
                dac2.set_range(dac_val);
                break;

                case 2:
                dac3.set_range(dac_val);
                break;
            }
            command_dac_range = false;
        }

        else if(command_tri){
            generate_sawtooth_wave();
            command_tri = false;
        }
    // }
    }
}


void generate_sawtooth_wave()
{
    for (int wave = 0; wave < tri_steps; wave++)
    {
        float voltage;

        if (tri_forward)
        {
            // Positive wave
            for (voltage = 0.0f + tri_bias_voltage; voltage <= tri_amplitude + tri_bias_voltage; voltage += tri_increasement)
            {
                if (tri_x)
                    dac1.write_voltage(voltage);
                else
                    dac2.write_voltage(voltage);

            }

            // Zero
            if (tri_x)
                dac1.write_voltage(0.0f + tri_bias_voltage);
            else
                dac2.write_voltage(0.0f + tri_bias_voltage);
        }
        else
        {
            // Negative wave
            for (voltage = tri_bias_voltage; voltage >= (tri_bias_voltage - tri_amplitude); voltage -= tri_increasement)
            {
                if (tri_x)
                    dac1.write_voltage(voltage);
                else
                    dac2.write_voltage(voltage);
            }

            // back to mid point
            if (tri_x)
                dac1.write_voltage(tri_bias_voltage);
            else
                dac2.write_voltage(tri_bias_voltage);
        }
    }
    tud_cdc_n_write(0, "TRIOK\r\n", 7);
    tud_cdc_n_write_flush(0);
}

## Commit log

2025-09-24 init commit
    [Connector_Base.SLDPRT, Connector_Base.STEP, Connector_Side.SLDPRT, Connector_Side.STEP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]
2025-09-25 materials added.
    [full_assemble.SLDASM]
